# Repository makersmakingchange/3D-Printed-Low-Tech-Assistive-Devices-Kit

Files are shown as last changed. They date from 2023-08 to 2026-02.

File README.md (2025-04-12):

# 3D-Printed Low Tech Assistive Devices Kit

The [3D Printed Low Tech Assistive Devices Kit](https://www.makersmakingchange.com/s/product/3d-printed-low-tech-assistive-devices-kit/01tJR000000690QYAQ) is an introduction to 3D printed devices. It is great for OT’s, Not-For-Profits, or Users who want to trial a few different devices. The assorted devices in this kit can be used for people of all ages. These devices can be altered by size, and colour giving the user flexibility for the devices to be a fit for them.

## 3D Printed Low Tech Assistive Devices Kit
### Summary

| Name                 | MMC Library Link | GitHub Repository Link |
|----------------------|----------------------------------------------------------------------------------|------------------------------------------------------ |
| Bottle Opener        | https://www.makersmakingchange.com/s/product/bottle-opener/01tJR00000068z0YAA    | https://github.com/makersmakingchange/Bottle-Opener   |   
| Key Turner           | https://www.makersmakingchange.com/s/product/key-turner/01tJR00000068z6YAA       | n/a                                                   |
| Pen Ball             | https://www.makersmakingchange.com/s/product/pen-ball/01tJR00000068zzYAA         | https://github.com/makersmakingchange/Pen-Ball        |
| Palm Pen Holder      | https://www.makersmakingchange.com/s/product/palm-pen-holder/01tJR00000068z8YAA  | https://github.com/makersmakingchange/Palm-Pen-Holder |
| Tube Opener          | https://www.makersmakingchange.com/s/product/tube-opener/01tJR00000068zxYAA      | https://github.com/makersmakingchange/Tube_Opener     |
| Bag Carrier          | https://www.makersmakingchange.com/s/product/bag-carrier/01tJR00000068yzYAA      | https://github.com/makersmakingchange/Bag-Carrier     |

### Bottle Opener
This device provides a large gripping surface and clamps onto the caps of standard water bottles with a small squeeze, allowing users to remove or screw on water bottle caps.

### Key Turner
Users loop their finger through the hole and twist to lock and unlock doors with minimal wrist movement. The large key bed can accommodate various shape of key heads.

### Pen Ball
The pen ball makes it easier to grip a pen, pencil, or other writing utensils.

### Palm Pen Holder
Users can gently curl their fingers around a handle to hold it securely or hook their thumb around the writing utensil

### Tube Opener
A tool used to help open small lids for anyone that has difficulty gripping and twisting the caps.

### Signature Guide
Aid that helps people to write on a specific spot for purposes such as writing a name, signature, or initials.

### Bag Carrier
Can assist people with arthritis or other disabilities to carry plastic bags and other grocery bags.

---

<!-- ABOUT MMC START -->
## About Makers Making Change
[Makers Making Change Logo](https://www.makersmakingchange.com/)

Makers Making Change is a program of [Neil Squire](https://www.neilsquire.ca/), a Canadian non-profit that uses technology, knowledge, and passion to empower people with disabilities.

Makers Making Change leverages the capacity of community based Makers, Disability Professionals and Volunteers to develop and deliver affordable Open Source Assistive Technologies.

 - Website: [www.MakersMakingChange.com](https://www.makersmakingchange.com/)
 - GitHub: [makersmakingchange](https://github.com/makersmakingchange)
 - Bluesky: [@makersmakingchange.bsky.social](https://bsky.app/profile/makersmakingchange.bsky.social)
 - Instagram: [@makersmakingchange](https://www.instagram.com/makersmakingchange)
 - Facebook: [makersmakechange](https://www.facebook.com/makersmakechange)
 - LinkedIn: [Neil Squire Society](https://www.linkedin.com/company/neil-squire-society/)
 - Thingiverse: [makersmakingchange](https://www.thingiverse.com/makersmakingchange/about)
 - Printables: [MakersMakingChange](https://www.printables.com/@MakersMakingChange)

### Contact Us
For technical questions, to get involved, or to share your experience we encourage you to [visit our website](https://www.makersmakingchange.com/) or [contact us](https://www.makersmakingchange.com/s/contact).
<!-- ABOUT MMC END -->

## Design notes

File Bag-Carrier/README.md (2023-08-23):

# Bag Carrier
## Device Details
## Overview 

The bag carrier is a low-cost, 3D-printed handheld tool that distributes the weight of bags carried. This 3D Printed Assistive Device can assist people with arthritis or other disabilities to carry plastic bags and reusable bags. The bag handles can easily loop around the two curved hooks. The handle is rounded to allows users to comfortably grip the carrier.

## Usage 

This handle is used to assist in carrying plastic or reusable bags by offering a wider grip. This handle can either be carried in hand or can attach onto the side of a wheelchair.

## Build Instructions 

All documentation, design files, and photos can be found on the GitHub page that is linked at the top of this project page. The Maker Checklist found in Documents will aid you in following the correct steps to build and work with the requester.

### SKILLS REQUIRED 
3D Printing

### TOOLS 

3D Printer

### 3D PRINTING 

The design prints in PLA with no supports. 3D print STL's and instructions can be found on the GitHub page linked at the top of this project page.

## Sizing

There are small, medium, and large handles available for different sized hands. A downloadable sizing guide can be found in the User Guide located at the top of this page in Documents.

## Attribution

Kerilyn Kennedy - Makers Making Change

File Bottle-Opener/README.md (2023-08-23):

# Bottle-Opener
The Bottle Opener is a simple, low-cost, 3D-printable handheld tool to help those with arthritis, limited finger dexterity or other related disabilities open or close plastic screw-on caps on various beverage bottles, cleaning products, condiments. The bottle opener allows users to remove or replace the lids of these jugs with a small squeeze on a large, rounded gripping surface. The Bottle Opener has several modified versions to open different sizes of containers. The different sizes are named by the approximate diameter of the caps they can open in millimeters.

Bottle_Opener

## More info at
- [Makers Making Change Project Page](https://makersmakingchange.com/project/bottle-opener/)
- [Makers Making Change Forum Thread](https://makersmakingchange.com/forum/topic/bottle-opener-for-arthritis)

## Getting Started

### 1. Print the 3D Printable components

Print the components according to the instructions in the [3D Print Guide](/Documentation/Bottle_Opener_3D_Print_Guide_V1.0.pdf).

All of the files and individual print files can be in the [/Build_Files](/Build_Files) folder.

### 2. Sizing

There are 5 different sizes of bottle opener to suit the different sizes of plastic caps on various bottles and containers. The [Summary](/Documentation/Bottle_Opener_Summary_V1.0.pdf) contains information on examples of different bottles that can be opened with the different sizes of bottle openers. A [Printable Sizing Sheet](/Documentation/Bottle_Opener_Printable_Sizing_Chart.pdf) has been provided to match bottle caps to the suitable bottle opener. Make sure to check "actual size" in the print settings so the image remains to-scale.

### 3. Bill of Materials

The [Bill of Materials](/Documentation/Bottle_Opener_BOM_V1.0.csv) lists the cost of building the different sizes of Bottle Openers.

## Files
### Documentation
| Document              | Version | Link |
|-----------------------|---------|------|
| Summary               | 1.0     | [Bottle_Opener_Summary](/Documentation/Bottle_Opener_Summary_V1.0.pdf)     |
| 3D Print Guide        | 1.0     | [Bottle_Opener_3D_Print_Guide](/Documentation/Bottle_Opener_3D_Print_Guide_V1.0.pdf)     |
| Design Rationale      | 1.0     | [Bottle_Opener_Design_Rationale](/Documentation/Bottle_Opener_Design_Rationale_V1.0.pdf)     |
| Bill of Materials     | 1.0     | [Bottle_Opener_Bill_of_Materials](/Documentation/Bottle_Opener_BOM_V1.0.csv)     |
| Maker Checklist       | 1.0     | [Bottle_Opener_Maker_Checklist](/Documentation/Bottle_Opener_Maker_Checklist_V1.0.pdf)     |
| User Guide            | 1.0     | [Bottle_Opener_User_Guide](/Documentation/Bottle_Opener_User_Guide_V1.0.pdf)    |
| Changelog             | 1.0     | [Bottle_Opener_Changelog](/Documentation/Bottle_Opener_Changelog_V1.0.pdf)     |
| Printable Sizing Chart| 1.0     | [Bottle_Opener_Printable_Sizing_Chart](/Documentation/Bottle_Opener_Printable_Sizing_Chart.pdf)     |

### Design Files
[CAD Files](/Design_Files)

### Build Files
 - [3D Printing Files](/Build_Files)

## Attribution
Designers:
 - Neil Squire / Makers Making Change

## License
<br /><span xmlns:dct="http://purl.org/dc/terms/" property="dct:title">Bottle Opener</span> by <a xmlns:cc="http://creativecommons.org/ns#" href="www.makersmakingchange.com" property="cc:attributionName" rel="cc:attributionURL">Neil Squire</a> is licensed under a <a rel="license" href="http://creativecommons.org/licenses/by-sa/4.0/">Creative Commons Attribution-ShareAlike 4.0 International License</a>.

## About Us
Makers Making Change Logo

Makers Making Change is an initiative of [Neil Squire](https://www.neilsquire.ca/), a Canadian non-profit that helps people with disabilities.

We are committed to creating a network of volunteer makers who support people with disabilities in their communities through 3D printing assistive devices. Check out our library of free, open-source assistive technologies with parts and build instructions.

 - [www.MakersMakingChange.com](https://www.makersmakingchange.com/)
 - [GitHub](https://github.com/makersmakingchange)
 - [Thingiverse](https://www.thingiverse.com/makersmakingchange/about)
 - Twitter: [@makermakechange](https://twitter.com/makermakechange)
 - Instagram: [@makersmakingchange](https://www.instagram.com/makersmakingchange)

## Contact Us

For technical questions, to get involved, or share your experience we encourage you to visit the [MMC Project Page]( https://www.makersmakingchange.com/project), [MMC Forum](https://forum.makersmakingchange.com), or contact info@makersmakingchange.com

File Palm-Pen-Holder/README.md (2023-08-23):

# Palm-Pen-Holder
There are multiple sizes available for this device for both the device size and pen hole size. If you are requesting this device, please indicate which size you believe will work the best for you. There is a sizing guide seen below and available for download. **If you want to customize the sizes further download and save both the ".scad" and ".json" files in the same place and use OpenSCAD to edit using the instructions found in the documention folder above**

# Overview
This is a customizable (parametric) 3D printable writing aid. The Palm Pen Holder makes it easier to grip a pen, pencil, or other writing utensil and may be useful for someone who has difficulty holding a pen or pencil directly. The device is able to be slid onto the hand of the user or gripped in various positions. The multiple sizing allows for various writing utensils and hand sizes.
# Usage
A pen or pencil is inserted through the Palm Pen Holder pen hole and is fixed in place by tightening a set screw to allow for different writing utensil sizes. The device can be gripped in multiple ways and also gently squeezes the hand for stability when writing. With different sizing available, this device works well with narrow writing utensils like paintbrushes or wider ones like sharpie markers. In addition, the device itself has alternate sizing to provide options for the user.

# Build Instructions
All documentation, design files, and photos can be found on the GitHub page that is linked at the top of this project page. The Maker Checklist document will aid you in following the correct steps to build and work with the requestor.

# SKILLS REQUIRED

3D Printing

# BILL OF MATERIALS

To assemble the Palm Pen Holder, you will need:

1x 3D Printed Palm Pen Holder

1x M4 machine screws, 20 mm long ($1.25 – $2.50) 

1x M4 hex nuts ($0.25)  

1x Writing utensil (pen, pencil, etc)

# TOOLS

Screwdriver

3D printer

# 3D PRINTING

The design prints in ABS or PLA with no support. 3D print STL’s and instructions can be found on the GitHub page linked at the top of this project page.

# CUSTOMIZATION
The design is parametric, which means that the size of the device itself the size of the pen hole can be modified by changing numbers in OpenSCAD. The editable OpenSCAD file can be found on the GitHub page linked at the top of the project page along with instructions within the documentation.

# Sizing:
There are small, medium, and large-sized Palm Pen Holder available for different hand sizes. In addition, the pen hole diameter can also be changed from narrow, standard, and wide. By use of the set screw, the writing utensil does not need to be the exact size of the pen hole but rather the sizing is available to fit large writing devices like markers and narrow ones such as fine paintbrushes. Sizing Charts can be found below and in addition, downloading the to scale document will allow one to see the outline of the different sizes to determine the ideal size.

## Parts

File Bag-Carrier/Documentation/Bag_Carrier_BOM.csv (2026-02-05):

Bag Carrier |  | Total Cost | Total Print time (hr) | Total filament (g)
Version: V2.0.1 | Last updated: 2024-Mar-27 | #DIV/0! | 2.23 | 41
Commercial Parts:
 | Part Name | Quantity Needed | Pkg Quantity | Price per package | Price per Unit | Price for qty needed | Link
<None> |  |  |  |  | #DIV/0! | #DIV/0!
 |  |  |  |  | #DIV/0! | #DIV/0!
 |  |  |  |  | #DIV/0! | #DIV/0!
3D Printed Parts ESTIMATED PRICING USING 1KG ROLL COST: | $25.00
Part | Description | Quantity Needed | TOTAL Mass (g) | Estimated Price | Print Time (Min) | Link
Large Bag Carrier - small and medium will cost slightly less |  | 1 | 41 | $1.03 | 134
 |  |  |  | $-
 |  |  |  | $-
 |  |  |  | $-
 |  |  |  | $-
 |  |  | Total Print Cost: | $1.03
Tools for Assembly
<None>
s
Alternatives (if there are other sources for some parts link them below)
Part and description | Link

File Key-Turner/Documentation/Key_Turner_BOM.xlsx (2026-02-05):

Device: | Key Turner
Version: | V1.0
Last Updated: | 2026-02-04
 |  |  |  |  |  |  |  | Total filament (g) |  | Unit Cost | Total Estimated Cost | Build Cost
 |  |  |  |  |  |  |  | 12.44 |  | $1.69 | $8.45
ID | Commercial Parts |  |  |  |  |  |  |  |  | $1.38 | $8.14
 | Part | Description |  | Manufacturer | Supplier | QTY / Device | QTY / PKG | PKGs | $/ PKG | $ / Device | Total Estimated Cost |  | Link
 |  | M4 x 12 mm bolt |  |  |  | 1 | 5 | 1 | $3.99 | $0.80 | $3.99 |  | https://www.homehardware.ca/en/5-pack-m4-x-12mm-zinc-plated-pan-head-machine-screws/p/2122013
 |  | M4 hex nut |  |  |  | 1 | 1 | 1 | $0.18 | $0.18 | $0.18 |  | https://www.homedepot.ca/product/paulin-m4-0-70-class-8-metric-hex-nut-din-934-zinc-plated/1000128515
 |  | M4 Washer |  |  |  | 2 | 20 | 1 | $3.97 | $0.40 | $3.97 |  | https://www.homedepot.ca/product/paulin-metric-flat-washers-4mm-20pcs/1001588032
 | 3D Printed Parts |  |  |  |  |  |  | 12.44 |  | $0.31 | $0.31
 | Part | Description | Filament Type | Filament | Color | QTY / Device | Mass (g) / Part | Total Mass | $ / kg | $ / Device | Total Estimated Cost |  | Link
 | Key_Turner.stl | Key turner body | PLA |  | Any | 1 | 12.44 | 12.44 | $25.00 | $0.31 | $0.31
 | Tools | *Tools are only required when attaching the key to the key turner*
 | Tool | Description |  | Manufacturer | Supplier |  |  |  |  |  |  |  | Link
 | Screw driver | Screwdriver that matches the head of the bolts purchased
 | Wrench/pliers | To hold the nut while tightening the bolt
 | Alternatives
 | Part | Description |  | Manufacturer | Supplier | QTY / Device | QTY / PKG | PKGs | $/ PKG | $ / Device | Total Estimated Cost |  | Link
 |  | #8-1/2" bolt |  |  |  | 1
 |  | #8 hex nut |  |  |  | 1
 |  | #8 washers |  |  |  | 2

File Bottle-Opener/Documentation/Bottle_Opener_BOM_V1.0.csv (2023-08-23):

Device: Bottle_Opener |  | Total Cost | Total Print time (hr) | Total filament (g)
Version: V1.0 | Date Created: 5/18/2022 | $4.65 | 3.78 | 37
3D Printed Parts ESTIMATED PRICING USING 1KG ROLL COST: | $25.00
Part | Description | Quantity Needed | TOTAL Mass (g) | Estimated Price | Print Time (Min) | Link
Bottle_Opener_30.stl | STL file for full functional bottle opener with nominal diameter of approx. 30 mm. | 1 | 37 | $0.93 | 227 | Bottle-Opener/Build_Files at main · makersmakingchange/Bottle-Opener (github.com)
Bottle_Opener_35.stl | STL file for full functional bottle opener with nominal diameter of approx. 30 mm. | 1 | 36 | $0.90 | 224
Bottle_Opener_40.stl | STL file for full functional bottle opener with nominal diameter of approx. 30 mm. | 1 | 36 | $0.90 | 226
Bottle_Opener_45.stl | STL file for full functional bottle opener with nominal diameter of approx. 30 mm. | 1 | 38 | $0.95 | 231
Bottle_Opener_50.stl | STL file for full functional bottle opener with nominal diameter of approx. 30 mm. | 1 | 39 | $0.98 | 241
 |  |  | Total Print Cost: | $4.65

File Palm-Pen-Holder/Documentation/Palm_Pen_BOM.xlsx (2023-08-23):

Device: Palm Pen Holder |  | Total Cost | Total Print time (hr) | Total filament (g)
Version: V1.0 | Date Created: 06/30/2023 | $1.72 | 8.33 | 50
Commercial Parts:
Part type (Electrical. Mechanical, Sanitization, ect) | Part Name | Quantity Needed | Pkg Quantity | Price per package | Price per Unit | Price for qty needed | Link
Hardware | M4- 0.70 Machine Screw Nut | 1 | 16 | $2.97 | $0.19 | $0.19 | https://www.homedepot.ca/product/paulin-metric-hex-nut-m4-70-16pcs/1001588036
Hardware | M4- 0.70 X 16 Machine Screw | 1 | 12 | $3.47 | $0.29 | $0.29 | https://www.homedepot.ca/product/paulin-pan-square-machine-screw-m4-70-x-16-12pcs/1001588009
3D Printed Parts ESTIMATED PRICING USING 1KG ROLL COST: | $25.00
Part | Description | Quantity Needed | TOTAL Mass (g) | Estimated Price | Print Time (Min) | Link
x_Palm_Pen_y_Pen_hole.STL Where “x” is the Palm Pen Holder device sizing and “y” is the pen hole sizing | File including the single piece Palm Pen Holder device | 1 | 50 | $1.25 | 500
 |  |  | Total Print Cost: | $1.25
Tools for Assembly
3D Printer
Screw Driver
Alternatives (if there are other sources for some parts link them below)
Part and description | Link
Note that some printers are less accurate and M4 size hardware may not fit. It is recommended that you go to a hardware store and test different bolt sizes for the palm pen that is created

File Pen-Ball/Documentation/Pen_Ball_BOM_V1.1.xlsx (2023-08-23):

Pen Ball |  | Total Cost | Total Print time (hr) | Total filament (g)
Version: V1.1 | Last Updated: 2023-Jun-30 | $3.07 | 8.33 | 47
Commercial Parts:
Part type (Electrical. Mechanical, Sanitization, ect) | Part Name | Quantity Needed | Pkg Quantity | Price per package | Price per Unit | Price for qty needed | Link
Hardware | M4- 0.70 Machine Screw Nut | 4 | 16 | $2.97 | $0.19 | $0.74 | https://www.homedepot.ca/product/paulin-metric-hex-nut-m4-70-16pcs/1001588036
Hardware | M4- 0.70 X 16 Machine Screw | 4 | 12 | $3.47 | $0.29 | $1.16 | https://www.homedepot.ca/product/paulin-pan-square-machine-screw-m4-70-x-16-12pcs/1001588009
3D Printed Parts ESTIMATED PRICING USING 1KG ROLL COST: | $25.00
Part | Description | Quantity Needed | TOTAL Mass (g) | Estimated Price | Print Time (Min) | Link
x_Pen_ball_y_Pen_hole.STL Where “x” is the pen ball sizing and “y” is the pen hole sizing | Pen ball STL includes both top and bottom of pen ball | 1 | 47 | $1.18 | 500
 |  |  | Total Print Cost: | $1.18
Tools for Assembly
3D Printer
Screw Driver
Alternatives (if there are other sources for some parts link them below)
Part and description | Link
Note that some printers are less accurate and M4 size hardware may not fit. It is recommended that you go to a hardware store and test different bolt sizes for the palm pen that is created

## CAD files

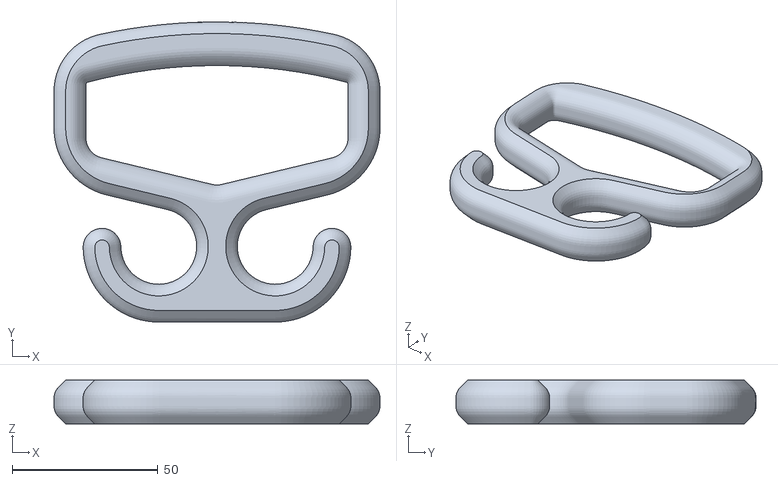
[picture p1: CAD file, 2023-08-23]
Bag-Carrier/3D_Print_Files/Bag_Carrier_Medium.stl
112.0 x 103.1 x 15.0

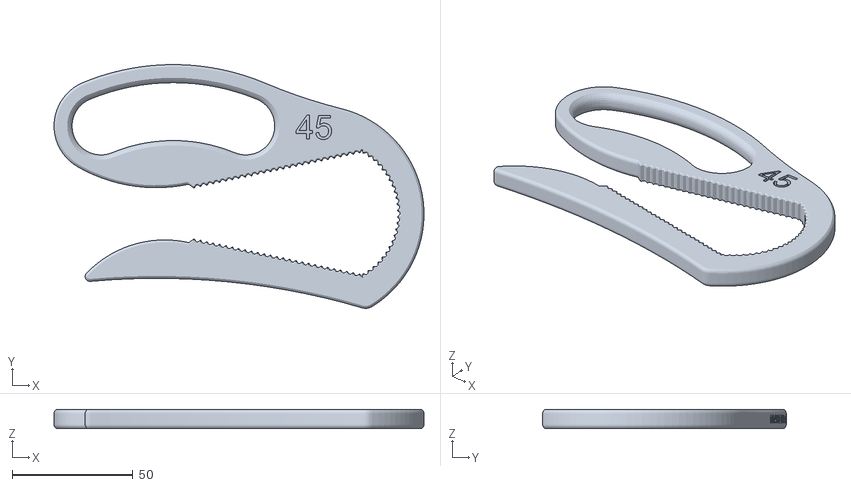
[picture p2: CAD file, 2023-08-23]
Bottle-Opener/Build_Files/Bottle_Opener_45.stl
153.5 x 101.2 x 8.00

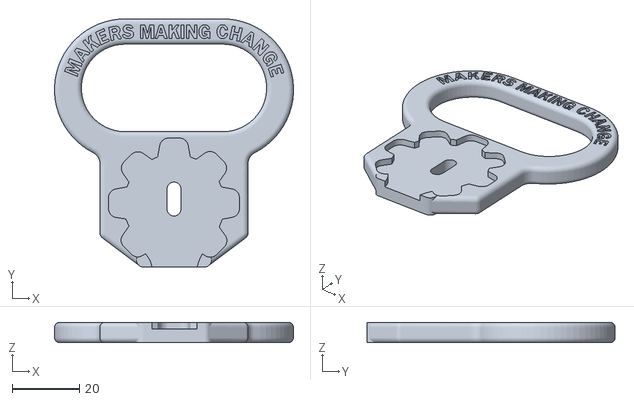
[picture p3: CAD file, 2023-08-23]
Key-Turner/Build_Files/3D_Print_Files/Key_Turner.stl
71.0 x 73.7 x 6.00

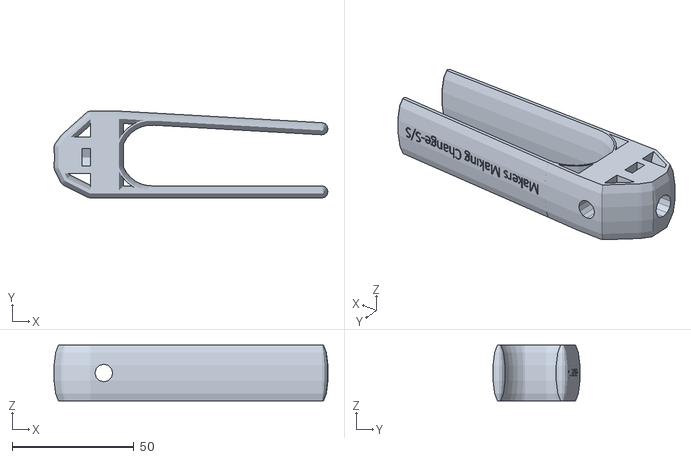
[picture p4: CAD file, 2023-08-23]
Palm-Pen-Holder/Build_Files/3D_Print_ Files/Small_Palm_Pen_Small_Pen_hole.stl
112.7 x 35.8 x 23.0

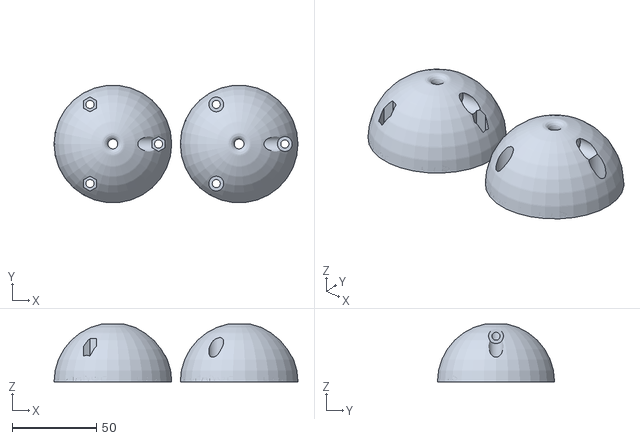
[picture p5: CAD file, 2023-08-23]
Pen-Ball/Build_Files/3D_Print_Files/Large_Pen_ball_Small_Pen_hole.stl
144.9 x 69.6 x 34.4

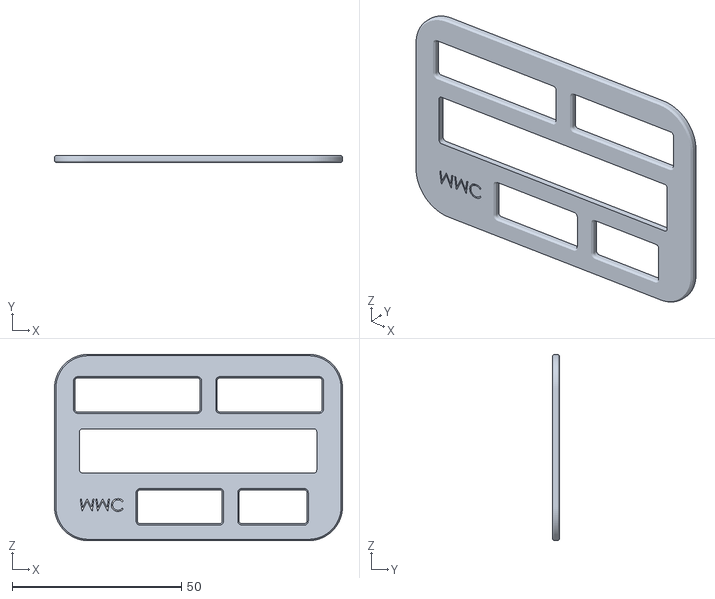
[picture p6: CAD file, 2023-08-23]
Signature-Guide/Build_Files/3D_Printing_Files/Signature_Guide_v1.1.0.stl
85.0 x 2.00 x 55.0

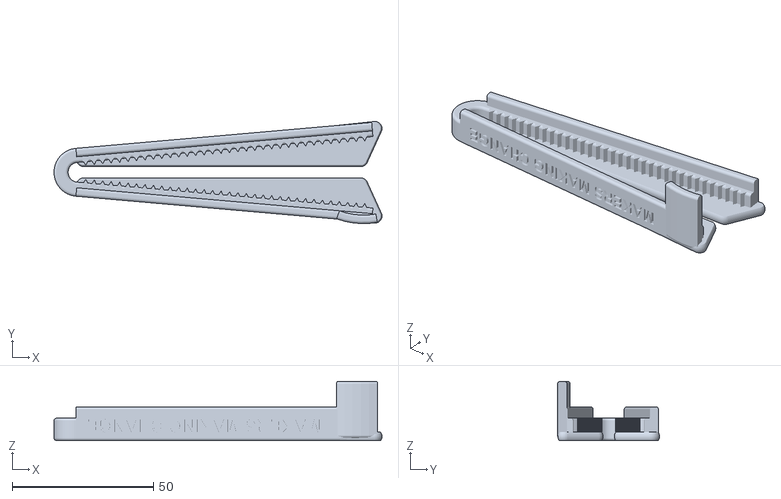
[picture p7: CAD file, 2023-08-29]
Tube-Opener/Build_Files/3D_Printing_Files/Tube_Opener.stl
116.0 x 36.1 x 21.0

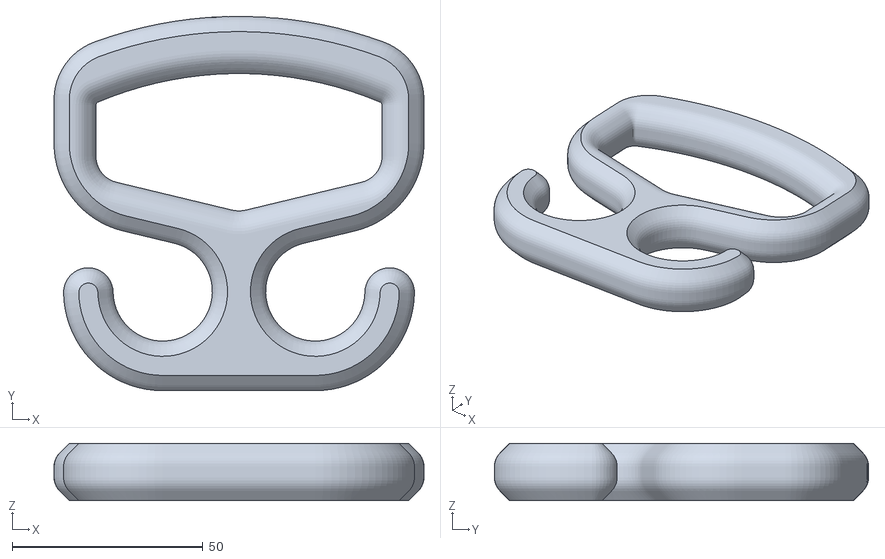
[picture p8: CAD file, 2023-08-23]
Bag-Carrier/3D_Print_Files/Bag_Carrier_Small.stl
97.0 x 98.1 x 15.0

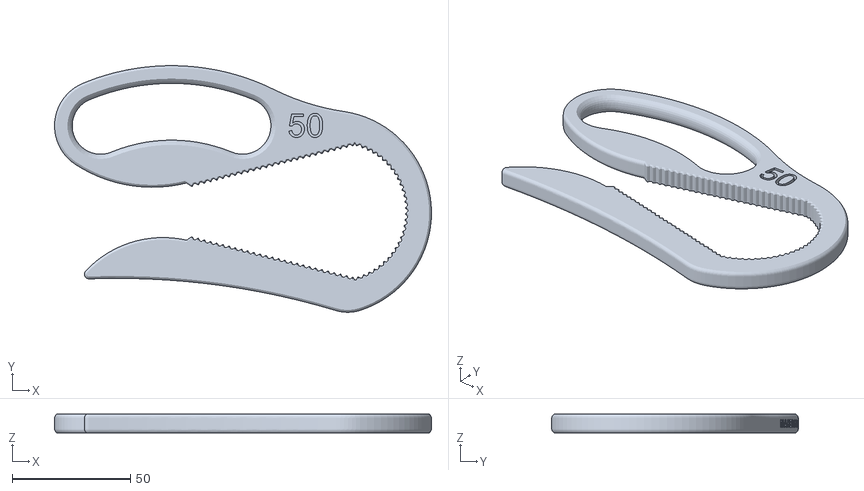
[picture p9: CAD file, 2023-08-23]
Bottle-Opener/Build_Files/Bottle_Opener_50.stl
159.5 x 104.4 x 8.00

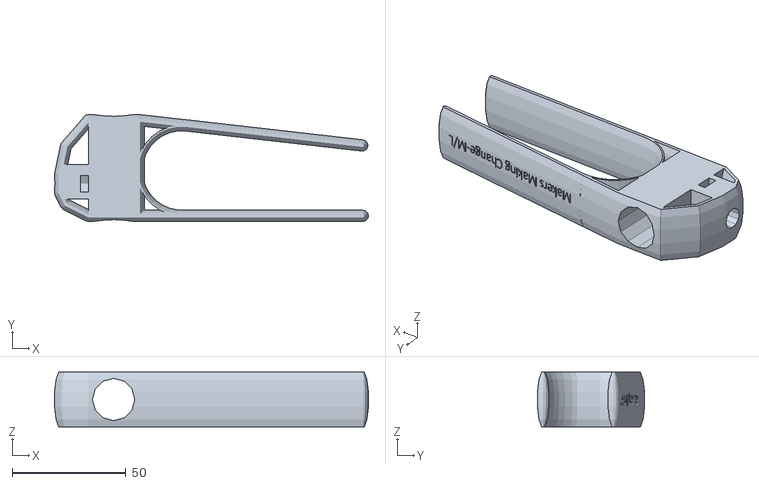
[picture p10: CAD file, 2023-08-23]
Palm-Pen-Holder/Build_Files/3D_Print_ Files/Med_Palm_Pen_Large_Pen_hole.stl
138.2 x 47.2 x 24.0

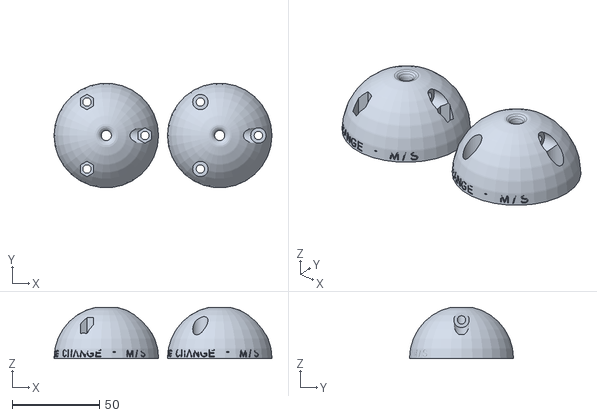
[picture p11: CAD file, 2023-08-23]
Pen-Ball/Build_Files/3D_Print_Files/Medium_Pen_ball_Small_Pen_hole.stl
124.9 x 59.6 x 29.3

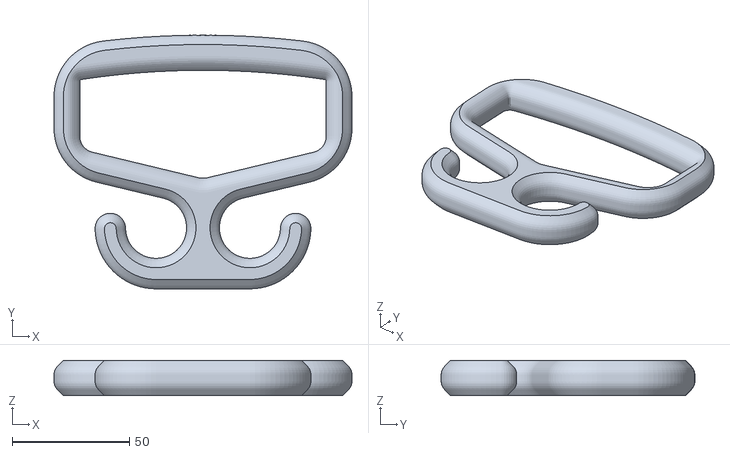
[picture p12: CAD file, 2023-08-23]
Bag-Carrier/3D_Print_Files/Bag_Carrier_Large.stl
127.0 x 108.1 x 15.0

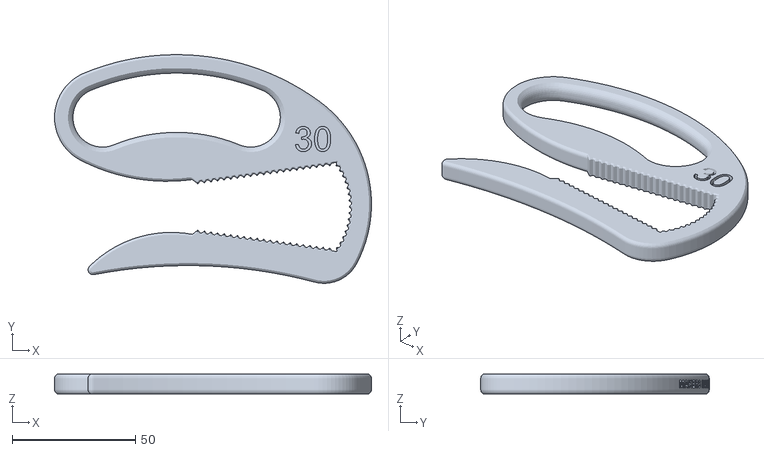
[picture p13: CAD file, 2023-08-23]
Bottle-Opener/Build_Files/Bottle_Opener_30.stl
128.6 x 92.7 x 8.00

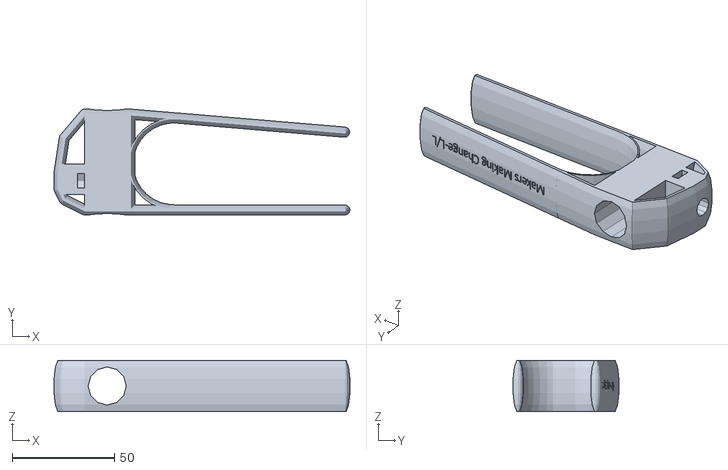
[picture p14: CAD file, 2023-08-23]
Palm-Pen-Holder/Build_Files/3D_Print_ Files/Large_Palm_Pen_Large_Pen_hole.stl
144.7 x 51.8 x 25.0

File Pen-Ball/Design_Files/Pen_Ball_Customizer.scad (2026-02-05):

// parametric pen ball - scruss 2018-03
// CC BY-SA - Stewart Russell - scruss.com
// for Makers Making Change - http://makersmakingchange.com/

// you will need:
// * 5 off M4 x 12 stainless pan head machine screws
// * 5 off M4 stainless nuts

// ** the two main parameters **
// may produce a useless design, so change at your own risk
ball_diam = 60.0;   // 60 mm is default; can go to 45 if wall_thick reduced
pen_diam = 10.5;    // should fit most pens; 10.5 mm is default

// ** lesser parameters
wall_thick = 2.0;   // shell thickness; default 2, reduce to 1 for 45 mm diameter
tol=0.8;            // tolerance for loose fit
// *** NB: please do not explicitly set $fn ***
// and everything below here: HERE BE (smallish) DRAGONS

/* M4 nut and screw dimensions - sized for M4 x 12

Nut: 7 mm across flats, 3.2 mm thick
so across points = 7 / ((√3) / 2) ~= 8.1 mm
source: http://www.fairburyfastener.com/xdims_metric_nuts.htm

Screw:          4.0 mm, 4.7 to outside of thread
Length:        12 or 20 mm
Head height:    3.1 mm
Head diameter:  8.0 mm
source: https://spaenaur.com/pdf/sectionR/R11.pdf
*/
nut_thick =          3.2;
nut_flats =          7.0;
nut_diam =          nut_flats / (sqrt(3)/2);
screw_length =      12.0;            // M4 x 12
screw_nom_diam =     4.0;
screw_head_diam =    8.0;
screw_head_thick =  nut_thick;   // for simplicity
pillar_height =     screw_length - (1.25 * nut_thick);

/* bolt passages:
   since we're on a sphere, the height at
   radius x is given by
   
   y = 2 × √(r² - x²)
   
   this drops off very quickly as x → r
   so we probably won't need this
*/
function height_at_radius(d, r) = 2 * sqrt(pow(d / 2, 2) - pow(r, 2));
pillar_diam = nut_diam + 2 * tol + wall_thick;
pillar_at_radius = (ball_diam - 2 * wall_thick - pillar_diam) / 2;
height_at_pillar = height_at_radius(ball_diam, pillar_at_radius);
catch_offset = pillar_at_radius;
echo(pillar_diam=pillar_diam, pillar_at_radius=pillar_at_radius, height_at_pillar=height_at_pillar, catch_offset=catch_offset);

//engraving variables
chars = "MAKERS MAKING CHANGE";
chars2 = "MAKERSMAKINGCHANGE.COM";
radius = (ball_diam/2)-3;
myPi = 3.14159;
chars_per_circle = 40;
step_angle = 360 / chars_per_circle;
circumference = 2 * PI * radius;
char_size = circumference / chars_per_circle;
char_thickness = 1;

module inprofile() {
    // rather than using a sphere, rotate_extrude a 2D path
    offset(r=-3 * wall_thick/2, $fn=16)difference() {
        circle(d=ball_diam, center=true, $fn=32);
        translate([-(ball_diam-(pen_diam + tol))/2, 0])square(ball_diam, center=true);
    }
}

module profile() {
    // 2D path for profile; looks like a letter D, kinda
    union() {
        difference() {
            offset(r=3 * wall_thick / 2, $fn=16)inprofile();
            offset(r=wall_thick / 2, $fn=16)inprofile();
        }
        translate([ball_diam / 2 - wall_thick, 0])square(wall_thick, center=true);
    }
}

module pillars() {
    // solid pillars we shoot the screw/nut holes through
    for(i=[0:2]) {
        rotate([0, 0, i * 120])translate([pillar_at_radius, 0, 0])cylinder(d=pillar_diam, h=2*height_at_pillar, center=true);
    }
}
            
module stiffeners() {
    // pen pipe stiffeners: two, 120 deg apart
    for(i=[0:1]) {
        rotate([0,0,30 + i * 120])rotate([-90, 0, 0])translate([0, 0, (pen_diam + wall_thick)/2])cylinder(d=screw_nom_diam, h=pillar_at_radius);
    }
}

module catch_reinforce() {
    // this is ugly: make a block to take pen-holding screw/nut
    //  but angled so you can print without support
    rotate([90, 0, 0])linear_extrude(height=pillar_diam, center=true)polygon([
    [ pen_diam / 2, catch_offset ],
    [ pen_diam / 2, catch_offset - pillar_diam / 2],
    [ pillar_at_radius, 0 ],
    [ pen_diam / 2, -(catch_offset - pillar_diam / 2)],
    [ pen_diam / 2, -catch_offset ],
    [ pen_diam / 2, -ball_diam/2 ],
    [ ball_diam/2, -ball_diam/2 ],
    [ ball_diam/2, ball_diam/2 ],
    [ pen_diam / 2, ball_diam/2 ],
    ]);
}

module inside_bits() {
    // all of the interior detail, clipped to the outer shell size
    intersection() {
        union() {
            stiffeners();
            pillars();
            catch_reinforce();
        }
        rotate_extrude()offset(r=wall_thick, $fn=16)inprofile();
    }
}

module screw_holes() {
    // three holes around edge: these are negative spaces
    // nut holes have six sides ('cylinder ... $fn=6') as
    // we emulate hex nuts that way: low-poly cylinders!
    for(i=[0:2]) {
        translate([pillar_at_radius * cos(i * 120), pillar_at_radius * sin(i * 120), 0]) {
            cylinder(d=screw_nom_diam + tol, h=ball_diam, center=true, $fn=32);
            translate([0, 0, pillar_height/2])rotate([0, 0, 30])cylinder(d=nut_diam + tol, h=ball_diam, $fn=6);
            translate([0, 0, -1*(ball_diam + pillar_height/2)])cylinder(d=screw_head_diam + tol, h=ball_diam, $fn=32);
        }
    }
}

module nut_catches() {
    // negative space for pen grip screw holes and nut catches
    // top screw hole
    translate([0, 0, catch_offset])rotate([90, 0, 90])union() {
        cylinder(d=screw_nom_diam + tol, h=ball_diam, $fn=32);
        translate([0,0,screw_length+1])cylinder(d=screw_head_diam + tol, h=ball_diam, $fn=32);
        // top nut catch
        translate([0,0,(pen_diam + tol + wall_thick) / 2])hull() {
            rotate([0, 0, 30])cylinder(d=nut_diam + tol, h=nut_thick + tol, $fn=6);
            translate([0, -ball_diam / 2, 0])rotate([0, 0, 30])cylinder(d=nut_diam + tol, h=nut_thick + tol, $fn=6);
        }
    }
    // bottom screw hole
    translate([0, 0, -catch_offset])rotate([90, 0, 90])union() {
        cylinder(d=screw_nom_diam + tol, h=ball_diam, $fn=32);
        translate([0,0,screw_length+1])cylinder(d=screw_head_diam + tol, h=ball_diam, $fn=32);
        // bottom nut catch
        translate([0,0,(pen_diam + tol + wall_thick) / 2])hull() {
            rotate([0, 0, 30])cylinder(d=nut_diam + tol, h=nut_thick + tol, $fn=6);
            translate([0, ball_diam / 2, 0])rotate([0, 0, 30])cylinder(d=nut_diam + tol, h=nut_thick + tol, $fn=6);
        }
    }
}

module shell() {
    // assemble all the things!
    difference() {
        union() {
            // the positive bits
            rotate_extrude()profile();  // outer shell
            inside_bits();              // interior detail
			}
			//engraving text
			for(i = [0 : chars_per_circle - 1]) {
    rotate(i * step_angle) 
        translate([0, radius + char_size / 2, 3]) 
            rotate([90, 0, 180]) linear_extrude(char_thickness) text(
                chars[i], 
                font = "Courier New; Style = Bold", 
                size = char_size, 
                valign = "center", halign = "center"
            );
        }//for (end engraving)
        union() {
            // the negative bits
            screw_holes();              // edge holes
            nut_catches();
        }
    }
}

module slice() {
    // split ball across middle and place halves side by side
    // (lower half flipped) for easy printing
    union() {
        translate([-(ball_diam + pen_diam) / 2, 0, 0]) {
            difference() {
                shell();
                translate([0, 0, -0.6 * ball_diam])cube(1.2 * ball_diam, center=true);
                			//engraving text
			for(i = [0 : chars_per_circle - 1]) {
    rotate(i * step_angle) 
        translate([0, radius + char_size / 2, 3]) 
            rotate([90, 0, 180]) linear_extrude(char_thickness) text(
                chars[i], 
                font = "Courier New; Style = Regular", 
                size = char_size, 
                valign = "center", halign = "center"
            );
        }//for (end engraving)
				}
        }
        translate([(ball_diam + pen_diam) / 2, 0, 0]) {
            difference() {
                rotate([180, 0, 0])shell();
                translate([0, 0, -0.6 * ball_diam])cube(1.2 * ball_diam, center=true);
							//engraving text
			for(i = [0 : chars_per_circle - 1]) {
    rotate(i * step_angle) 
        translate([0, radius + char_size / 2, 3]) 
            rotate([90, 0, 180]) linear_extrude(char_thickness) text(
                chars2[i], 
                font = "Courier New; Style = Bold", 
                size = char_size, 
                valign = "center", halign = "center"
            );
        }//for (end engraving)
            }
        }
    }
}

slice(); // generate the sliced module

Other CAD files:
Pen-Ball/Build_Files/3D_Print_Files/Large_Pen_ball_Medium_Pen_hole.stl
Bottle-Opener/Build_Files/Bottle_Opener_35.stl
Palm-Pen-Holder/Build_Files/3D_Print_ Files/Med_Palm_Pen_Small_Pen_hole.stl
Pen-Ball/Build_Files/3D_Print_Files/Medium_Pen_ball_Large_Pen_hole.stl
Pen-Ball-main/Version Archive/Version 1/Pen_Grip_Ball.scad
Bottle-Opener/Build_Files/Bottle_Opener_40.stl
Palm-Pen-Holder/Build_Files/3D_Print_ Files/Large_Palm_Pen_Med_Pen_hole.stl
Palm-Pen-Holder/Build_Files/3D_Print_ Files/Large_Palm_Pen_Small_Pen_hole.stl
Palm-Pen-Holder/Build_Files/3D_Print_ Files/Med_Palm_Pen_Med_Pen_hole.stl
Palm-Pen-Holder/Build_Files/3D_Print_ Files/Small_Palm_Pen_Large_Pen_hole.stl
Palm-Pen-Holder/Build_Files/3D_Print_ Files/Small_Palm_Pen_Med_Pen_hole.stl
Pen-Ball/Build_Files/3D_Print_Files/Large_Pen_ball_Large_Pen_hole.stl
Pen-Ball/Build_Files/3D_Print_Files/Medium_Pen_ball_Medium_Pen_hole.stl
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

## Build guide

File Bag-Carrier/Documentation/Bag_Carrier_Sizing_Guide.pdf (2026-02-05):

V2.0.1 | MARCH 2024

## Bag Carrier

## SIZING GUIDE

© 2021-2024 by Neil Squire Society. This work is licensed under the CC BY SA 4.0 License: http://creativecommons.org/licenses/by-sa/4.0
Files available at https://github.com/makersmakingchange | Page 1 of 2

### Introduction

The Bag Carrier is a low-cost, 3D-printed handheld tool that distributes the weight of bags carried. This 3D Printed Assistive Device can assist people with arthritis or other disabilities to carry plastic bags and reusable bags. The Bag Carrier comes in 3 different sizes: small, medium, and large.

### Sizing

| Weight (g) | Dimensions (mm)
Width | Height | Grip Width | Thickness
Small | 35 | 97 | 96 | 75 | 46
Medium | 38 | 113 | 101 | 90 | 46
Large | 41 | 127 | 106 | 105 | 46

### Sizing Instructions

1. Print out the next page. It should be set to letter sized paper with no scaling.
2. With a ruler, measure the scale guideline to ensure that it was printed to scale.
3. Extend your hand out with your fingers together. Align the bottom section of your pointer finger with the line of the left of the hole of the handle. If your four fingers fit between the 2 lines, the handle should be large enough.
4. Select the appropriate size.

V2.0.1 | MARCH 2024

## Bag Carrier

## SIZING GUIDE

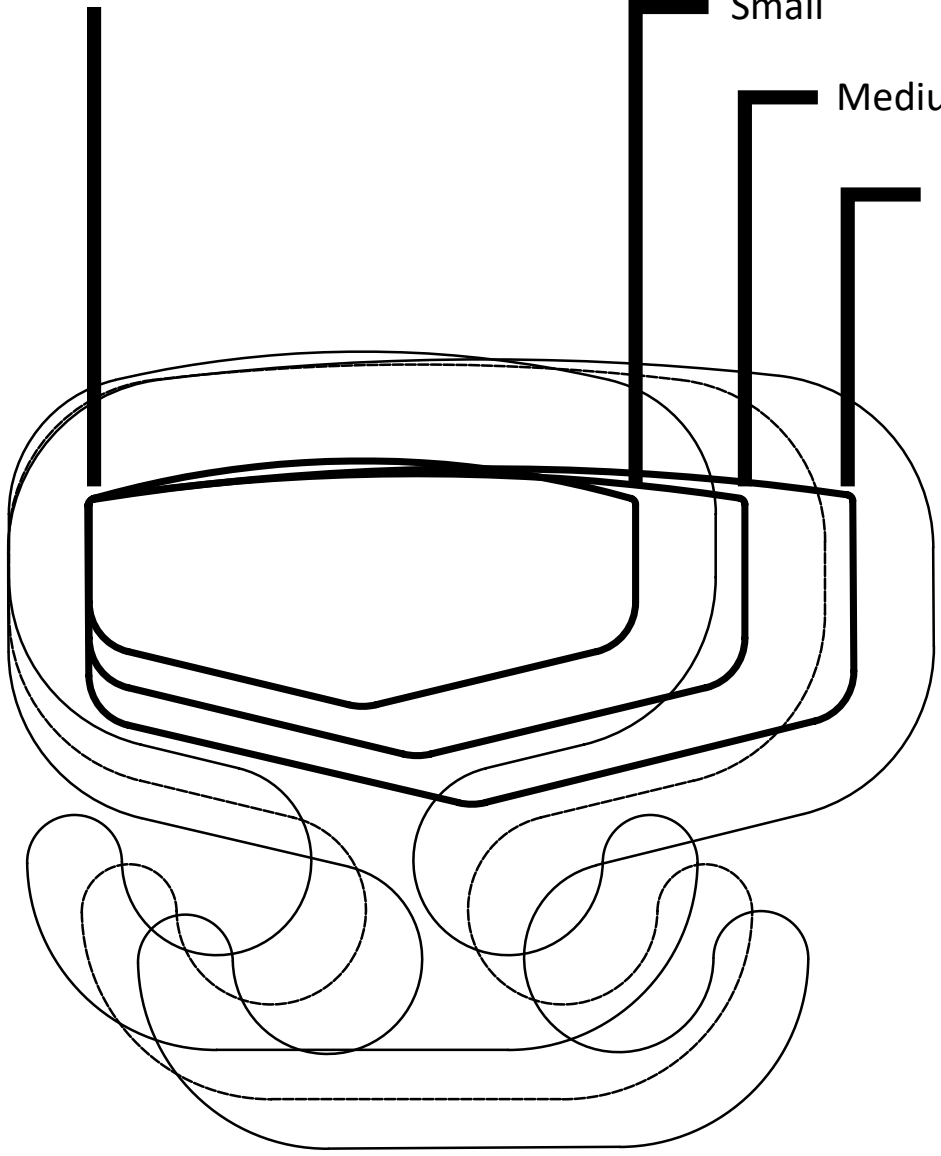
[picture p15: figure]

© 2021-2024 by Neil Squire Society. This work is licensed under the CC BY SA 4.0 License: http://creativecommons.org/licenses/by-sa/4.0
Files available at https://github.com/makersmakingchange | Page 2 of 2

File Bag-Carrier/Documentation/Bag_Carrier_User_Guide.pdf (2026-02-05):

V2.0.1 | MARCH 2024

## Bag Carrier

## USER GUIDE

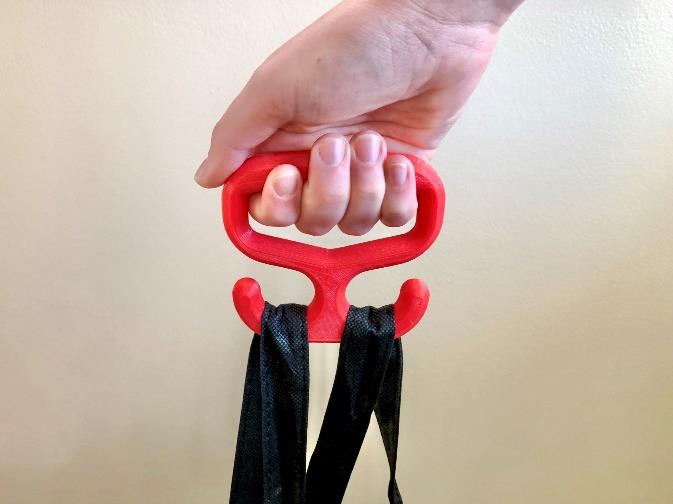
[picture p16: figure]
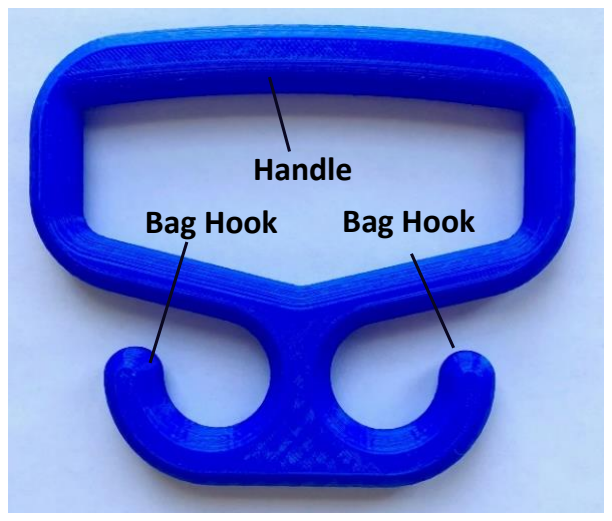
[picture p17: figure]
Handle; Bag Hook

© 2021-2024 by Neil Squire Society. This work is licensed under the CC BY SA 4.0 License: http://creativecommons.org/licenses/by-sa/4.0
Files available at https://github.com/makersmakingchange/Bag-Carrier | Page 1 of 1

### Introduction

The Bag Carrier is a low-cost, 3D-printed handheld tool that distributes the weight of bags carried. This 3D Printed Assistive Device can assist people with arthritis or other disabilities to carry plastic bags and reusable bags. The Bag Carrier comes in 3 different sizes: small, medium, and large.

### Features

### Usage

This handle is used to carry plastic or reusable bags. This handle can either be carried in hand or can attach onto the side of a wheelchair. The bag handles can easily loop around the two curved hooks.

### Compatibility

There are 3 different sized handles in order to try and accommodate many different hand sizes. Please refer to the Sizing Guide to determine which size handle will work best for you.

### Specifications

Version | Weight (g) | Dimensions (mm)
Overall Width | Overall Height | Grip Width | Thickness
Small | 35 | 97 | 96 | 75 | 46
Medium | 38 | 113 | 101 | 90 | 46
Large | 41 | 127 | 106 | 105 | 46

### Cleaning

The Bag Carrier can be cleaned with warm soapy water. Do not expose the device to high heat as it may deform or break. (i.e., do not put it in the dishwasher or washing machine).

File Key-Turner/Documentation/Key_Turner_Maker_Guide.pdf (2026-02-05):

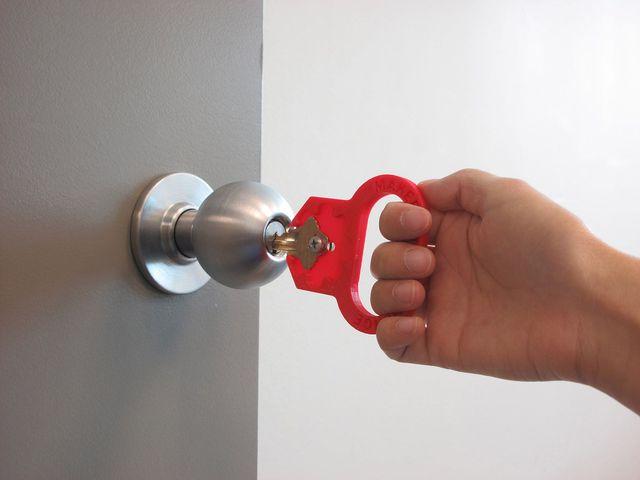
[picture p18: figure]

0.80 hrs

1 pcs

f

0.20 mm

k

0.40 mm

h

PLA

10 g

d

Prusa

MK3/S/S+

# Summary

Accessory for people with limited finger dexterity to hold keys.

Household (https://printables.com/model?categoryId=3) | > | Other House Equipment (https://printables.com/model?categoryId=45)
Tags: | hand | keychain | key | disability | arthritis
assistivetechnology | assistivedevice

The key turner is a low-cost, 3D-printed handheld tool for people with

arthritis or other disabilities to operate their keys.

Users loop their finger through the hole and twist to lock and unlock doors

with minimal wrist movement. The large key bed can accommodate

various shape of key heads.

### Print Settings

### Infill: 50%

Makers Making Change (https://printables.com/@MakersMakingChange)

# Key Turner

### VIEW IN BROWSER (https://printables.com/model/213712-key-turner)

updated 29. 8. 2023 | published 29. 8. 2023

# Model files

### Resolution: 0.2mm

### Supports: No

### Rafts: No

### Hardware Required:

1 M4 x 12mm screw (metric) / #8 - 1/2" screw (imperial)

1 M4 hex nut / #8 hex nut

2 M4 washer /#8 washer

### About Makers Making Change

Makers Making Change (https://makersmakingchange.com/) is an initiative of the Neil Squire Society, a

Canadian non-profit that empowers people with disabilities through

technology.

We leverage the capacity of community based Makers, (https://makersmakingchange.com/learn-how-our-community-works/) Disability

Professionals and Volunteers to develop and deliver affordable Open

Source Assistive Technologies. (https://makersmakingchange.com/assistive-devices/)

Volunteer (https://makersmakingchange.com/maker-wanted/) to print a device

Tackle (https://makersmakingchange.com/forum/forums/design-challenges/) a design challenge

Submit (https://makersmakingchange.com/submit-an-idea/) an assistive device idea

Follow us on Instagram, (https://www.instagram.com/makersmakingchange/) Facebook, (https://www.facebook.com/makersmakechange/) and Twitter (https://twitter.com/makermakechange)

•

•

•

key_turner.stl

# Print files

h PLA | k 0.40 mm | f 0.20 mm | 0.80 hrs | 10 g | d Prusa MK3/S/S+

# License

This work is licensed under a

Creative Commons (4.0 International License)

Attribution-ShareAlike (http://creativecommons.org/licenses/by-sa/4.0/)

### ✖ | Sharing without ATTRIBUTION

✔ | Remix Culture allowed
✔ | Commercial Use
✔ | Free Cultural Works
✔ | Meets Open Definition

key_turner_02mm_pla_mk3s_48m.gcode

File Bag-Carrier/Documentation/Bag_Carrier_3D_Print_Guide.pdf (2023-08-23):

V2.0 | FEB 2022

## Bag Carrier

## 3D PRINTING GUIDE

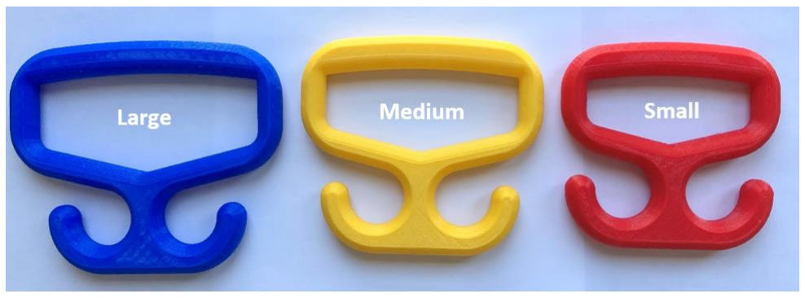
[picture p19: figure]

© 2021 by <Author>.
This work is licensed under the CC BY SA 4.0 License: http://creativecommons.org/licenses/by-sa/4.0
Files available at <Replace with MMC Library Link> | Page 1 of 1

### 3D Printing Summary

Metrics | Small | Medium | Large
Total Print Time (min) | 112 | 123 | 134
Total Number of Components | 1 | 1 | 1
Typical Total Mass (g) | 35 | 38 | 41
Typical Number of Print Setups | 1 | 1 | 1

### 3D Printing Settings

Print File Name | Qty | Total Print Time (hr:min) | Mass (g) | Infill (%) | Support (Y/N) | Layer Height/ Nozzle Diameter (mm) | Notes (orientation, special settings, etc)
Bag_Carrier_Small.stl | 1 | 1:52 | 35 | 20 | N | 0.3/0.4 | Print in orientation given in STL
Bag_Carrier_Medium.stl | 1 | 2:03 | 38 | 20 | N | 0.3/0.4 | Print in orientation given in STL
Bag_Carrier_Large.stl | 1 | 2:14 | 41 | 20 | N | 0.3/0.4 | Print in orientation given in STL

### Post-Processing

These handles are printed without supports; hence no post-processing is required.

### Customization Options

The user can request that the device be printed in multiple colours.

### Examples of Quality Prints

Below is a picture of what print quality is expected from printing this device.

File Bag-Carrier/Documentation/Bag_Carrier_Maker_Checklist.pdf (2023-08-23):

V2.0 FEB 2022

## Bag Carrier

## MAKER CHECKLIST

© 2021 by <Author>.
This work is licensed under the CC BY SA 4.0 License: http://creativecommons.org/licenses/by-sa/4.0
Files available at <Replace with MMC Library Link> | Page 1 of 1

## Maker To Do List

Ask the requester to print off the User Quick Guide so they can determine which size bag carrier would best fit them.
Determine the cost of materials and relay this cost to the user before printing to ensure the requester is comfortable with the price.
Ask the requester if they want any customizations to the device (e.g., color).
Print the device.
Deliver the device and User Quick Guide to the requestor.

## Items to Give to User

User Quick Guide
Bag Carrier

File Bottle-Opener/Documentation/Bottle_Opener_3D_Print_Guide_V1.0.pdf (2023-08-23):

V1.0| May 2022

## Bottle Opener

## 3D PRINTING GUIDE

© 2022 by Neil Squire / Makers Making Change. This work is licensed under the CC BY SA 4.0 License: http://creativecommons.org/licenses/by-sa/4.0 Files available at https://makersmakingchange.com/project/bottle-opener/

### 3D Printing Summary

Metrics
Total Print Time (min) | 224 - 241
Total Number of Components | 1 - 5
Typical Total Mass (g) | 36 - 39
Typical Number of Print Setups | 1 - 5

### 3D Printing Settings

Print File Name | Qty | Total Print Time (hr:min) | Mass (g) | Infill (%) | Support | Layer Height/ Nozzle Diameter(mm) | Notes (orientation, special settings, etc.)
Bottle_Opener_30.stl | 1 | 3:47 | 37 | 50 | No Support | 0.2/0.4 | Adjust number of perimeters to 3-4.
Bottle_Opener_35.stl | 1 | 3:44 | 36 | 50 | No Support | 0.2/0.4 | Adjust number of perimeters to 3-4.
Bottle_Opener_40.stl | 1 | 3:46 | 36 | 50 | No Support | 0.2/0.4 | Adjust number of perimeters to 3-4.
Bottle_Opener_45.stl | 1 | 3:51 | 38 | 50 | No Support | 0.2/0.4 | Adjust number of perimeters to 3-4.
Bottle_Opener_50.stl | 1 | 4:01 | 39 | 50 | No Support | 0.2/0.4 | Adjust number of perimeters to 3-4.

### Post-Processing

- Remove any burrs or sharp edges that may occur if applicable.

### Customization Options

- There are parameters given in the CAD file (.f3d) to change the cap size and handle size if desired.
- Can be printed in any colour.

## 3D PRINTING GUIDE

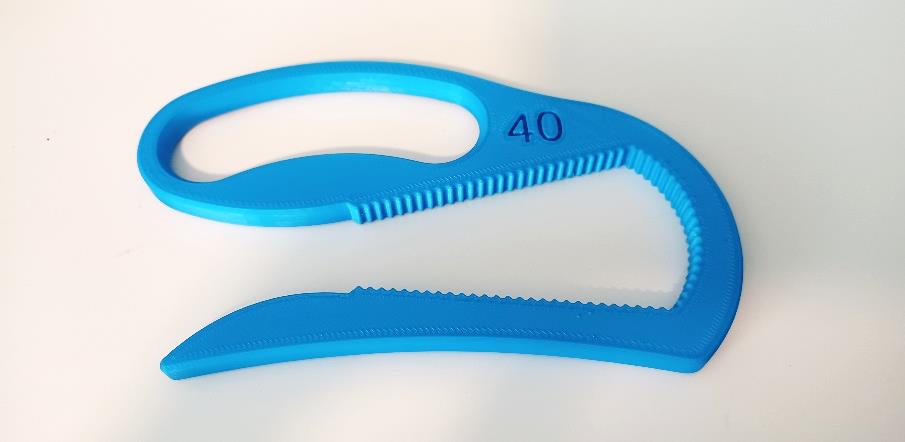
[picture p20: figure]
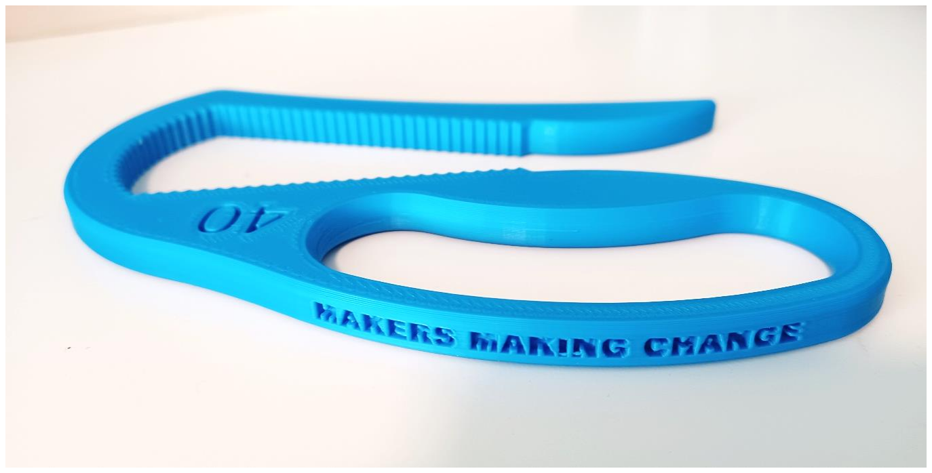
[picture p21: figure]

© 2022 by Neil Squire / Makers Making Change.

### Examples of Quality Prints:

Example of Bottle Opener 40

Example of Bottle Opener 40

## 3D PRINTING GUIDE

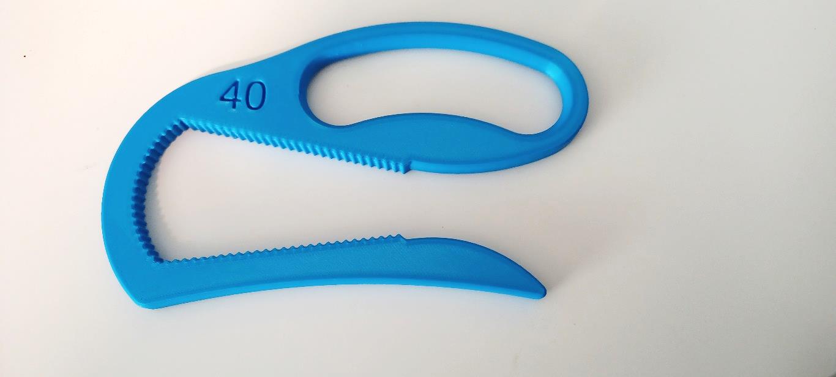
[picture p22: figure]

© 2022 by Neil Squire / Makers Making Change.

Example of Bottle Opener 40

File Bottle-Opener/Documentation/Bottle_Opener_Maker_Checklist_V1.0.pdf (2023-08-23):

V1.0 | May 2022

## Bottle Opener

## MAKER CHECKLIST

© 2022 by Neil Squire / Makers Making Change This work is licensed under the CC BY SA 4.0 License: http://creativecommons.org/licenses/by-sa/4.0 Files available at https://makersmakingchange.com/project/bottle-opener/

## Maker To Do List

Talk to User about which bottles they would like to open, determine which sizes of Bottle Opener to print using the Printable Sizing Chart or examples list.
Ask user about which colour they would prefer the device to be printed in.
Print and test the device/devices.
Print User Guide.

## Items to Give to User

Printed, tested device/devices. User Guide.

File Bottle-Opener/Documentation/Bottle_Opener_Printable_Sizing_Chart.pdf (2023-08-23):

To check if scale is correct,
the line below should be 100mm long.

50mm

45mm

40mm

35mm

30mm

# Printable Sizing Chart for Bottle Opener

To ensure a correct fit,

## bottle caps should fit

within the lines shown.

© 2022 by Neil Squire / Makers Making Change. This work is licensed under the CC BY SA 4.0 License: hp://creavecommons.org/licenses/by-sa/4.0
Files available at hps://makersmakingchange.com/project/bole-opener/ | Page 1 of 1

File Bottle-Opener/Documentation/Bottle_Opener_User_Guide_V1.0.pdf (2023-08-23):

V1.0 | May 2022

## Bottle Opener

## USER QUICK GUIDE

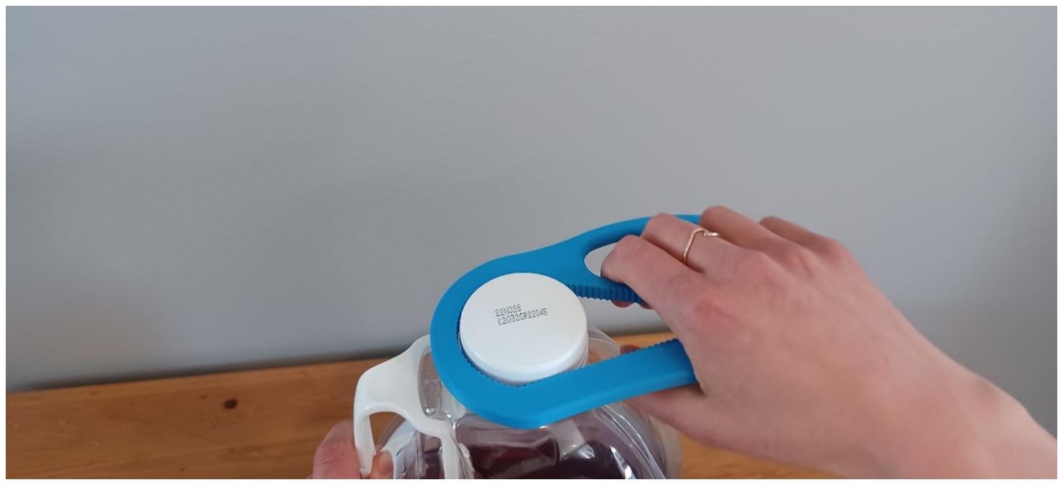
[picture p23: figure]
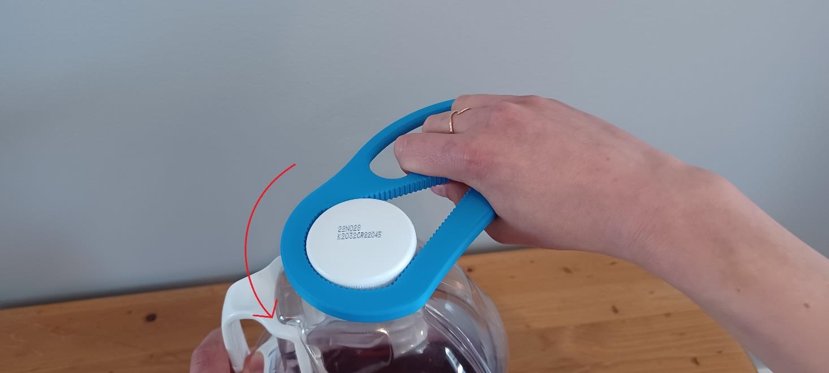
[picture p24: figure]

© 2022 by Neil Squire (https://neilsquire.ca/) / Makers Making Change. This work is licensed under the CC BY SA 4.0 License: http://creativecommons.org/licenses/by-sa/4.0 Files available at https://makersmakingchange.com/project/bottle-opener/

### Introduction

The Large Bottle Opener is a tool to help those with arthritis, limited finger dexterity or other related disabilities open the screw-on caps commonly seen on large juice jugs.

### Usage

Grip the bottle opener with fingers placed though the hole and palm on the bottom lever. Place the bottle opener over the lid of the bottle, squeeze the lever while twisting the cap off the bottle.

## USER QUICK GUIDE

© 2022 by Neil Squire (https://neilsquire.ca/) / Makers Making Change.

### Compatibility

Bottle Opener
Version

Compatible
Diameter of
Caps

Examples of compatible
Bottles and Containers
(May vary between brands)

Image Example of compatible Bottles

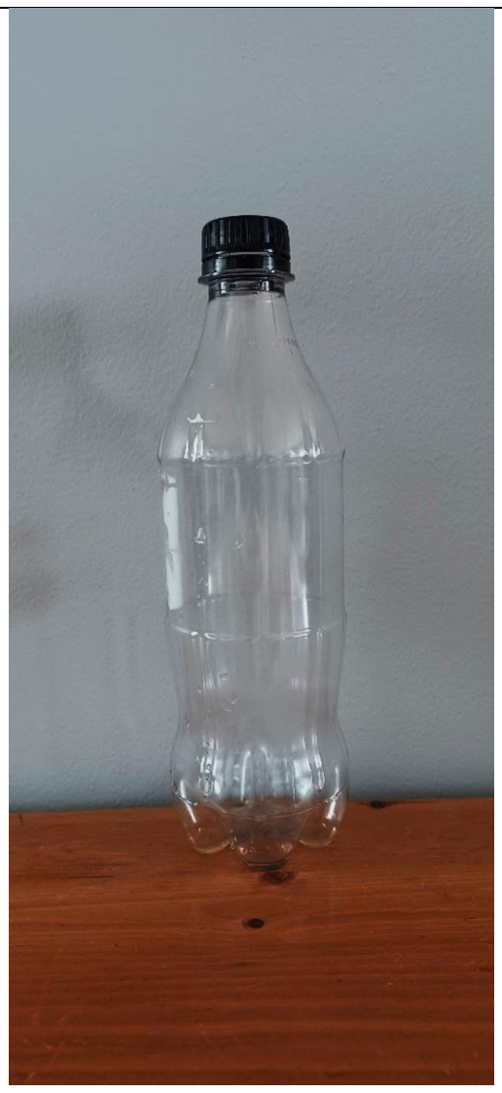
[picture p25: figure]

Bottle Opener
30 | 28 – 30 mm
- Pop bottles of all
sizes (355 mL to 2 L)
- Bottled Water of all
sizes (355 mL to 2 L)
- Milk Carton 2 L
- Juice Carton 2 L

## USER QUICK GUIDE

© 2022 by Neil Squire (https://neilsquire.ca/) / Makers Making Change.

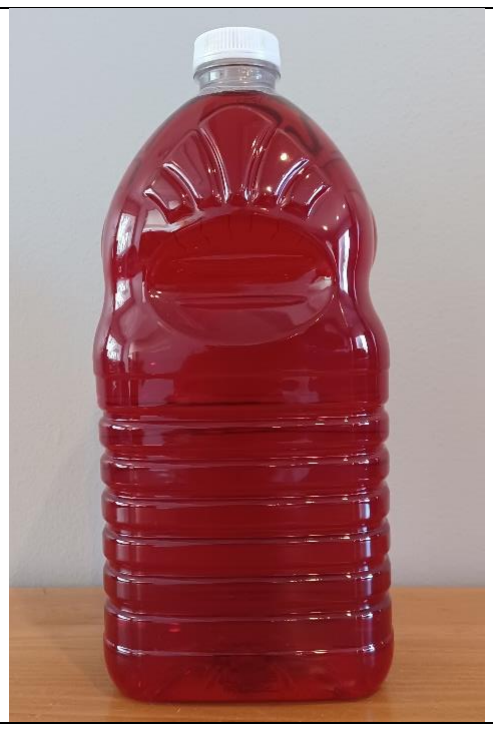
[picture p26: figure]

Bottle Opener 35 | 33 – 36 mm | • Juice Jug (Some brands) 1.89 L • Ketchup Bottle 1 L • Juice Carton 900 mL

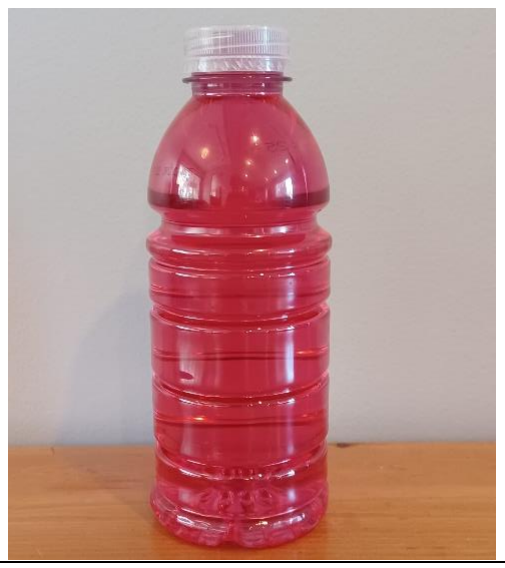
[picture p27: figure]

Bottle Opener 40 | 38 – 41 mm | • Sports Drink 591 mL • Sports Drink 950 mL • Juice Bottle 473 mL • Iced Tea Bottle 473 mL • Milk Bottle 473 mL • Milk Jug 2 L • Milk Jug 4 L • Kefir Bottle 1 L
Bottle Opener 45 | 43 – 46 mm | • Juice Jug 1.46 L • Juice Jug (Some Brands) 1.89 L • Juice Jug 945 mL

## USER QUICK GUIDE

© 2022 by Neil Squire (https://neilsquire.ca/) / Makers Making Change.

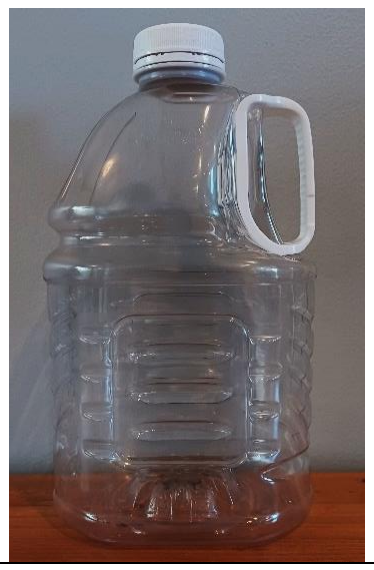
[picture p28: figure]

Bottle Opener
50 | 48 – 51 mm | • | 3 L Juice Jug

### Cleaning

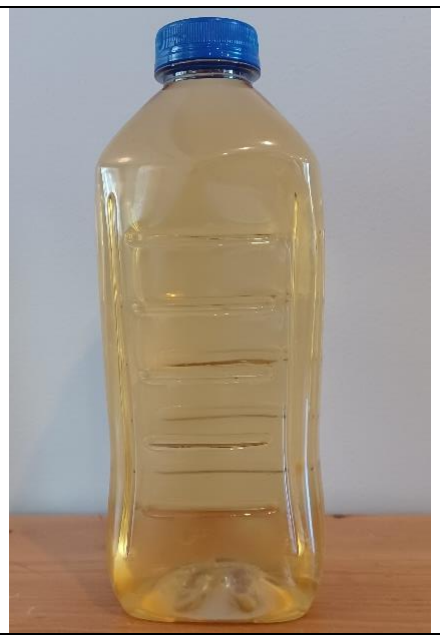
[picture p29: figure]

Clean with damp cloth, sterilize with disinfecting wipes or light spray. Do not submerge.

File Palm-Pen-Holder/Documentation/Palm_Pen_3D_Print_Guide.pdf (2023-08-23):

V1.0 | Sept 2021

## Palm Pen

## 3D PRINTING GUIDE

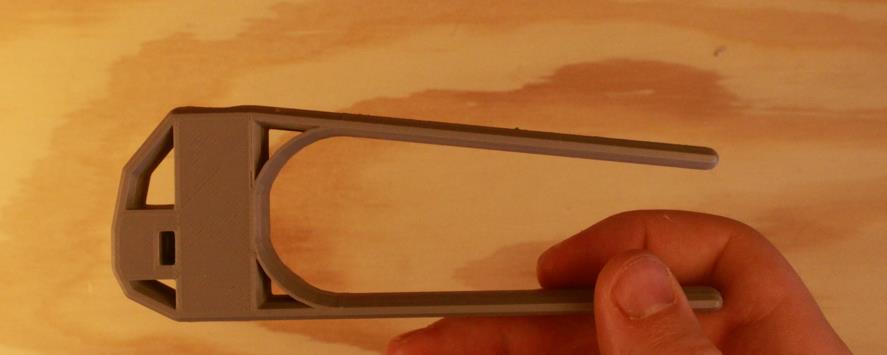
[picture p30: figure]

© 2022 by <Author>.

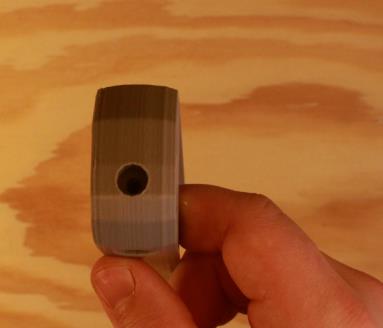
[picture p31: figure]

This work is licensed under the CC BY SA 4.0 License: http://creativecommons.org/licenses/by-sa/4.0
Files available at <Replace with MMC Library Link> | Page 1 of 1

### 3D Printing Summary

Palm Pen Size
Metrics | Small | Medium | Large
Total Print Time (min) | 170 | 200 | 240
Total Number of Components | 1 | 1 | 1
Typical Total Mass (g) | 23 | 30 | 35
Typical Number of Print Setups | 1 | 1 | 1

### 3D Printing Settings

Print File Name | Qty | Total Print Time (hr:min) | Mass (g) | Infill (%) | Support (Y/N) | Layer Height/ Nozzle Diameter (mm) | Notes (orientation, special settings, etc)
x_Palm_Pen_y_Pen_hole.S TL where “x” is the palm pen device sizing and “y” is the pen hole sizing | 1 | 170-240 | 23-35 | 20 | N | 0.2/0.4 | - Print in orientation given when brought onto slicer bed

### Post-Processing

- If you notice any blobs on the side of the device try using a blade to clean up the prints.

### Customization Options

- If different sizing is required for the pen hole or palm pen diameter the sizes can be altered using the OpenSCAD file found on the GitHub “design files” folder. Access to the GitHub can be found on the project page of this device.

### Examples of Quality Prints:

- Below are photos of what print quality is expected from printing this device.

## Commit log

2026-02-05 Updated files and folders
    - Added Action and file for automating
    - Removing superfluous files
    - Reorganizing files and folders to match current style
    [Bottle_Opener_30.f3d, Bottle_Opener_30.stl, Bottle_Opener_35.f3d, Bottle_Opener_35.stl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]
2026-02-05 Updating files
    - Removed superfluous files
    - Made sure other files are the most up-to-date versions
    - Reorganized files and folders to current format
    [Bag Carrier.f3d, Bag Carrier.step, Bag_Carrier_BOM.csv, Bag_Carrier_BOM.xlsx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]
